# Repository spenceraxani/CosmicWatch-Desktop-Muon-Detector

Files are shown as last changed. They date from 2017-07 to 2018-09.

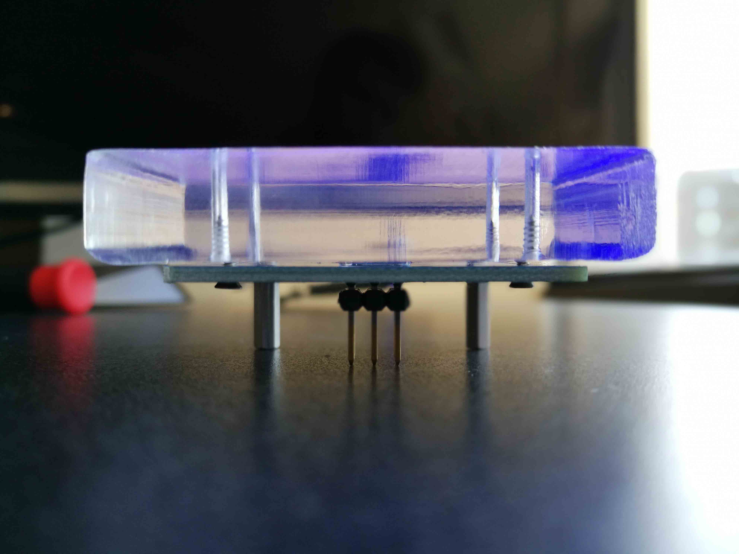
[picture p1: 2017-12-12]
Pictures/IMG_20171208_104722.jpg

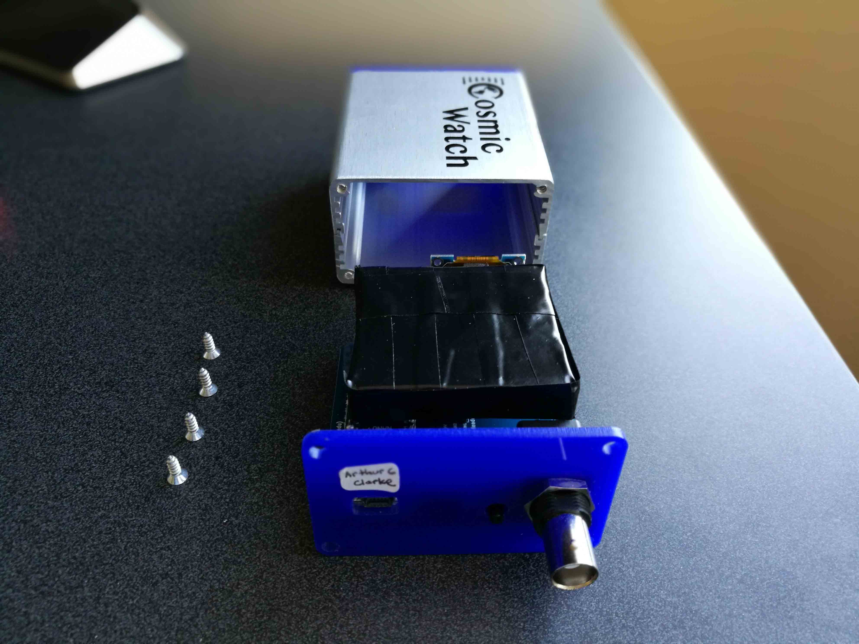
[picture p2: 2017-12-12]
Pictures/IMG_20171208_104146.jpg

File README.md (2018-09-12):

# (Outdated version) CosmicWatch-Desktop-Muon-Detector

The is an outdate version of the detector.
The latest version (v2) can be found here:
https://github.com/spenceraxani/CosmicWatch-Desktop-Muon-Detector-v2

This repository if for the supplementary material used to build the CosmicWatch Desktop Muon Detectors

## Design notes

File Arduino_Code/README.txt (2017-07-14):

This folder contains:
1. The Arduino Nano code. 
2. The CH340g driver from https://github.com/adrianmihalko/ch340g-ch34g-ch34x-mac-os-x-driver

In order to use the code, you must install the following libraries:
  1. Adafruit SSD1306     -- by Adafruit Version 1.0.1
  2. Adafruit GFX Library -- by Adafruit Version 1.0.2
  3. TimerOne             -- by Jesse Tane et al. Version 1.1.0

This can be done from the Arduino IDE: go to Tools, select
  1. Board = Arduino nano
  2. Port = the USB port that the Arduino is plugged into. If you don’t see it, you may need to install the CH340g driver

If you are using MAC OS, you need to also install the CH340g Driver. 

IF you are using Linux, you need to give permission to use your USB ports:
	In terminal: sudo chmod 666 /dev/ttyUSB0

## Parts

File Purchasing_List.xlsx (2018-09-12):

The following is the list of components used in the project. The links provided aren't necessarily the cheapest place to purchase the components, we've included it simply to indicate places where we have purchased them in the past.
Component List |  | Buy Extras
Item | Name | Required number | Discription | Link
1 | 49.9 Ohm resistor | 3 | RES SMD 49.9 OHM 1% 1/8W 0805 | Digikey Part Number: 311-49.9CRCT-ND
2 | 499 Ohm resistor | 1 | RES SMD 499 OHM 1% 1/8W 0805 | Digikey Part Number: 311-499CRCT-ND
3 | 1K resistor | 3 | RES SMD 1K OHM 1% 1/8W 0805 | Digikey Part Number: 311-1.00KCRCT-ND
4 | 10k resistor | 2 | RES SMD 10K OHM 1% 1/8W 0805 | Digikey Part Number: 311-10.0KCRCT-ND
5 | 100k resistor | 2 | RES SMD 100K OHM 1% 1/8W 0805 | Digikey Part Number: 311-100KCRCT-ND
6 | 226k resistor | 1 | RES SMD 226K OHM 1% 1/8W 0805 | Digikey Part Number: 311-226KCRCT-ND
7 | 5pF capacitor | 1 | CAP CER 5PF 50V NP0 0805 | Digikey Part Number: 1276-2552-1-ND
8 | 22pF capacitor | 1 | CAP CER 22PF 50V NP0 0805 | Digikey Part Number: 399-1113-1-ND
9 | 10nF capacitor | 5 | CAP CER 10000PF 50V X7R 0805 | Digikey Part Number: 311-1136-1-ND
10 | 0.1uF capacitor | 1 | CAP CER 0.1UF 50V X7R 0805 | Digikey Part Number: 399-1170-1-ND
11 | 0.47uF capacitor | 1 | CAP CER 0.47UF 50V X7R 0805 | Digikey Part Number: 399-8100-1-ND
12 | 1uF capacitor | 1 | CAP CER 1UF 50V Y5V 0805 | Digikey Part Number: 587-1308-1-ND
13 | 10uF capacitor | 1 | CAP CER 10UF 6.3V X5R 0805 | Digikey Part Number: 490-1718-1-ND
14 | 47uH inductor | 1 | FIXED IND 47UH 170MA 1.3 OHM SMD | Digikey Part Number: 490-4063-1-ND
15 | Schottky diode | 2 | DIODE SCHOTTKY 40V 500MA SOD123 | Digikey Part Number: MBR0540CT-ND
16 | 4 pin header | 1 | CONN FEMALE 4POS .100" R/A TIN | Digikey part number: S5440-ND
17 | 6-pin connector | 1 | 6-pin connector for SiPM PCB | Digikey Part Number: WM17457-ND
18 | 6-pin header | 1 | 6-pin header for Main PCB | Digikey Part Number: 1212-1229-ND
19 | Reset button | 1 | SWITCH TACTILE SPST-NO 0.02A 15V | Digikey part number: P12215S-ND
20 | BNC header | 1 | CONN BNC JACK R/A 50 OHM PCB | Digikey part number: WM5514-ND
21 | Standoff for SiPM PCB | 2 | 1/8" Hex Size, 3/8" Length, 0-80 Thread Size | McMasterCarr part number: 91780A027
22 | Standoff screws Main side | 4 | 0-80 Thread Size, 5/16" Long | McMasterCarr part number: 91771A056
23 | Plastic scintillator screws | 4 | 18-8 Stainless Steel, Number 0 Size, 5/16" Long | McMasterCarr part number: 92470A024
24 | DC-DC Booster | 1 | LT3461AES6#PBF | http://www.linear.com/product/LT3461A
25 | Op-Amp | 1 | LT1807IS8#PBF | http://www.linear.com/samples/LT1807
26 | 5mm LED | 1 | Any color, 5mm | https://www.amazon.com/gp/product/B01FDOBRU4/ref=ox_sc_act_title_2?ie=UTF8&psc=1&smid=A353AQG9I0DZD6
27 | Barrell Jack | 1 | 5.5mmx2.1mm 3Pins | https://www.amazon.com/gp/product/B00MJVIFS2/ref=ox_sc_act_title_4?ie=UTF8&psc=1&smid=AYQ5IQCXKV6BV
28 | 5mm LED holder | 1 | LED Light Mounting Holders | https://www.amazon.com/uxcell-Pieces-Plastic-Mounting-Holders/dp/B00K85965W
29 | Arduino Nano | 1 | ATmega328 CH340G | Check Ebay or Amazon
30 | OLED screen | 1 | 0.96" Inch I2c IIC OLED , 128x64 | https://www.amazon.com/Diymall-Serial-Display-Module-Arduino/dp/B01HHOAQ5A?s=electronics NOTE: VCC NEEDS TO BE THE 4th PIN ON THE OLED, IT CANNOT BE THE GND PIN. SOME MANUFACTURERS SWAP THE PINS.
31 | Tin Foil | 1 | 10x10cm of Aluminium foil for wrapping the Plastic scintilaltor | https://www.amazon.com/Reynolds-Wrap-Aluminum-Foil-Square/dp/B00UNT0Y2M
32 | Black electrical tap | ~1m | Black electrical tape for making the Plastic scintillator light-tight | https://www.amazon.com/Electrical-Tape-several-colors-Black/dp/B003ZWN5ZM
33 | Rubber feet | 4 | Silicon bumper for feet | https://www.amazon.com/VOVOV-Self-adhesive-Rubber-Bumpons-diameter/dp/B016GWHSBE
34 | SiPM | 1 | 6x6mm SiPM MicroFC-60035-SMT | http://sensl.com/estore/microfc-60035-smt/
35 | Plastic scintillator | 1 | 5x5x1 cm Plastic scintillator | You want something that peaks in the 400nm range.
36 | Optical Gel | <1ml | Small amount of optical gel. Vaciline might work. | Check ebay or amazon
37 | Aluminium Case (without faceplates) | 1 | Aluminium case, 2506H-2.9” | http://www.enclosuresandcasesinc.com/
38 | Main PCB + SiPM PCB | 1 | 2 layer, 10cm x 10cm, 1.6mm thickness, zipped files in PCB folder | https://www.elecrow.com/5pcs-2-layer-pcb.html
39 | Front and back faceplate | 1 | Endplates | You can 3d print them, or send the .dxf files to Elecrow and have them laser cut them. Or make them in a machine shop. Or http://www.enclosuresandcasesinc.com/ will make them

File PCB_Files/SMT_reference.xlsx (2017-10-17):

Main PCB
Component | value | Discription | Link | Comment
R1 | 10k | RES SMD 10K OHM 1% 1/8W 0805 | Digikey Part Number: 311-10.0KCRCT-ND | DC-DC Booster
R2 | 226k | RES SMD 226K OHM 1% 1/8W 0805 | Digikey Part Number: 311-226KCRCT-ND | DC-DC Booster
R3 | 499 | RES SMD 100 OHM 1% 1/8W 0805 | Digikey Part Number: 311-100CRCT-ND | Amplifying circuit
R4 | 1k | RES SMD 1K OHM 1% 1/8W 0805 | Digikey Part Number: 311-1.00KCRCT-ND
R5 | 10k | RES SMD 1K OHM 1% 1/8W 0805 | Digikey Part Number: 311-10.0KCRCT-ND | Amplifying circuit
R6 | 100k | RES SMD 100K OHM 1% 1/8W 0805 | Digikey Part Number: 311-100KCRCT-ND | Peak Detector Circuit
R7 | 100k | RES SMD 100K OHM 1% 1/8W 0805 | Digikey Part Number: 311-100KCRCT-ND | Peak Detector Circuit
R8 | 1k | RES SMD 1K OHM 1% 1/8W 0805 | Digikey Part Number: 311-1.00KCRCT-ND
R9 | 1k | RES SMD 1K OHM 1% 1/8W 0805 | Digikey Part Number: 311-1.00KCRCT-ND
D1 | 500ma diode | DIODE SCHOTTKY 40V 500MA SOD123 | Digikey Part Number: MBR0540CT-ND | Has direction
D2 | 500ma diode | DIODE SCHOTTKY 40V 500MA SOD123 | Digikey Part Number: MBR0540CT-ND | has direction
L1 | 47uH | FIXED IND 47UH 170MA 1.3 OHM SMD | Digikey Part Number: 490-4063-1-ND
C1 | 22pF | CAP CER 22PF 50V NP0 0805 | Digikey Part Number: 399-1113-1-ND | DC-DC Booster
C2 | 0.47uF | CAP CER 0.47UF 50V X7R 0805 | Digikey Part Number: 399-8100-1-ND | DC-DC Booster
C3 | 1uF | CAP CER 1UF 50V Y5V 0805 | Digikey Part Number: 587-1308-1-ND | DC-DC Booster
C4 | 10uF | CAP CER 10UF 6.3V X5R 0805 | Digikey Part Number: 490-1718-1-ND
C5 | 0.1uF | CAP CER 0.1UF 50V X7R 0805 | Digikey Part Number: 399-1170-1-ND
C6 | 10nF | CAP CER 1000PF 50V X7R 0805 | Digikey Part Number: 399-1147-1-ND | Peak Detector Circuit
C7 | 5pF | CAP CER 5pF 50V 0805 | Digikey Part Number: 1276-2552-1-ND
U1 | LT3461A | 3MHz booster | http://www.linear.com/product/LT3461A
U2 | LT1807IS8#PBF | 325MHz OpAmp | http://www.linear.com/product/LT1807
Reset | Reset button | SWITCH TACTILE SPST-NO 0.02A 15V | Digikey part number: P12215S-ND
Arduino_Nano | Arduino Nano | 16 MHz | Check Ebay or Amazon
BNC | BNC header | CONN BNC JACK R/A 50 OHM PCB | Digikey part number: WM5514-ND
OLED | 4 pin header | CONN FEMALE 4POS .100" R/A TIN | Digikey part number: S5440-ND
LED | LED light | Any color, 5mm | https://www.amazon.com/gp/product/B01FDOBRU4/ref=ox_sc_act_title_2?ie=UTF8&psc=1&smid=A353AQG9I0DZD6
Header | 6pin connector | SOCKET 7 MM SOLDER TAIL DOUBLE | Digikey Part Number: 1212-1229-ND
SiPM PCB
Component | value | Discription | Link | Comment
R1 | 49.9 | RES SMD 49.9 OHM 1% 1/8W 0805 | Digikey Part Number: 311-49.9CRCT-ND
R2 | 49.9 | RES SMD 49.9 OHM 1% 1/8W 0805 | Digikey Part Number: 311-49.9CRCT-ND
R2 | 49.9 | RES SMD 49.9 OHM 1% 1/8W 0805 | Digikey Part Number: 311-49.9CRCT-ND
C1 | 10 nF | CAP CER 10000PF 50V X7R 0805 | Digikey Part Number: 311-1136-1-ND
C2 | 10 nF | CAP CER 10000PF 50V X7R 0805 | Digikey Part Number: 311-1136-1-ND
C3 | 10 nF | CAP CER 10000PF 50V X7R 0805 | Digikey Part Number: 311-1136-1-ND
C4 | 10 nF | CAP CER 10000PF 50V X7R 0805 | Digikey Part Number: 311-1136-1-ND
U1 |  | SiPM MicroFC-60035-SMT | SENSL
Header | 6-pin connector | WM17457-ND | WM17457-ND

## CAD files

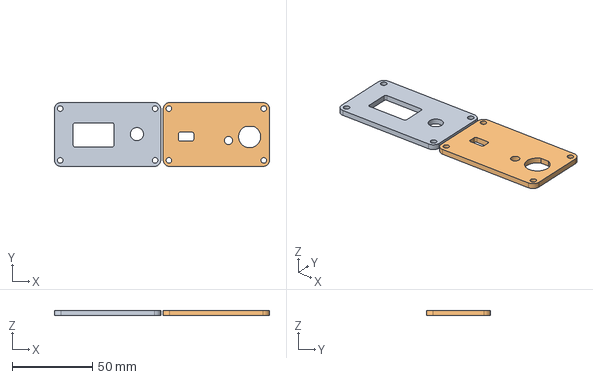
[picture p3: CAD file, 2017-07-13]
Enclosure_Files/Endplates.step
134.3 x 39.9 x 3.00 mm
Endplates
Endplates001

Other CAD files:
Enclosure_Files/Endplates.dxf
Enclosure_Files/Endplates.ipt
Enclosure_Files/Endplates.stl
Enclosure_Files/Endplates.stp

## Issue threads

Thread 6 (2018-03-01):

### ISSUE TITLE
Single LED and count on main board test

### ISSUE THREAD

**Issue by johnddias** [spenceraxani/CosmicWatch-Desktop-Muon-Detector#6]
Looking for any tips, please.  The main PCB is assembled and when I plug it in I see the LED blink once and the screen reports one measurement.  from the instructions I was expecting a solid LED and a negative count with the SPiM disconnected, what could be wrong?  Thanks

**Comment by spenceraxani** [comment]
Hi,

Not to worry, it’s probably fine. As long as you see that the CosmicWatch splash screen appears on the OLED and that you are seeing roughly +29.5V on the HV to GND pins on the 6-pin header , that’s about as much as you can test until you plug the SiPM in. 

An older version of the code wasn’t taking the dead time into account properly, and that is what was causing the negative count rate. This has been fixed with the updated Arduino code. 

Thanks,

Spencer

**Comment by johnddias** [comment]
Thanks Spencer.  I did get my SiPM ready and plugged in but getting the same result on the display.  I'm waiting for a scope to test things out before I give up hope.

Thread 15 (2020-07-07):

### ISSUE TITLE
PCB populating reference clarification

### ISSUE THREAD

**Issue by jparshook** [spenceraxani/CosmicWatch-Desktop-Muon-Detector#15]
On the PCB populating reference sheet, C14 is listed as a resistor (0 Ohm jumper) but is shown as a capacitor on the schematic. Could you please clarify the correct part for C14?

**Comment by spenceraxani** [comment]
Hi,

C14 can just be shorted with a 0Ohm resistor or a wire. 

Thanks,

Spencer

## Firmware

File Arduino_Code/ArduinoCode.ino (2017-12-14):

/*
Desktop Muon Counter Arduino Code
Questions?
Spencer N. Axani 
saxani@mit.edu

Requirements: Sketch->Include->Manage Libraries:
  1. Adafruit SSD1306     -- by Adafruit Version 1.0.1
  2. Adafruit GFX Library -- by Adafruit Version 1.0.2
  3. TimerOne             -- by Jesse Tane et al. Version 1.1.0
*/

#include <Adafruit_SSD1306.h>
#include <Adafruit_GFX.h>
#include <Wire.h>
#include <SPI.h>
#include <TimerOne.h>  
#include <EEPROM.h>

const byte OLED = 1;                    // Turn on/off the OLED [1,0] (Set to 0 to improve time)
const byte LED  = 0;                    // Turn on/off the LED delay [1,0] (Set to 0 to improve time)
const int SIGNAL_THRESHOLD = 20;        // Min threshold to trigger on
const int LED_BRIGHTNESS = 255;          // Change the brightness on the LED [0-255]. 5 is a dim value.


//This calibration is for 499, 5pF, 10k
//const float cal[] = {4.0614902396231111e-14, -7.8414735932155768e-11, 5.6819206951234577e-08, -1.7873823684604088e-05, 0.0029455520399522652, 0.01701073093454207, 26.268331951783924};
//This calibration is for 499, 5pF, 10k
const float cal[] = {9.038130548712698e-15, -1.4599909946491252e-12, -1.2626490003703338e-08, 1.1406923013075114e-05, -0.002891003749200569, 0.5003740521722947, 15.615470780166067};


//INTERUPT SETUP
#define TIMER_INTERVAL 1000000          // Every 1,000,000 us the timer will update the clock on the screen

//OLED SETUP
#define OLED_RESET 10             
Adafruit_SSD1306 display(OLED_RESET);   // Setup the OLED


//initialize variables
char detector_name[40];

unsigned long time_stamp                      = 0L;
unsigned long measurement_deadtime            = 0L;
unsigned long time_measurement                = 0L;      // Time stamp
unsigned long interrupt_timer                 = 0L;      // Time stamp
unsigned long start_time                      = 0L;      // Reference time for all the time measurements
unsigned long total_deadtime                  = 0L;      // total measured deadtime
unsigned long waiting_t1                      = 0L;
unsigned long measurement_t1;
unsigned long measurement_t2;
float sipm_voltage =0;
unsigned long count                           = 0L;      // A tally of the number of muon counts observed
float last_sipm_voltage                          = 0;

byte waiting_for_interupt = 0;

void setup() {
  ADCSRA &= ~(bit (ADPS0) | bit (ADPS1) | bit (ADPS2));    // clear prescaler bits
  ADCSRA |= bit (ADPS1);                                   // Set prescaler to 4  
  Serial.begin(9600);
  
  display.begin(SSD1306_SWITCHCAPVCC, 0x3C);               // Begin the OLED screen
  
  if (OLED == 1)
  {
      display.setRotation(2);                       // 2 = upside down; 0 = rightside down
      OpeningScreen();
      delay(2000); 
      display.setTextSize(1);
  }
  
  pinMode(3, OUTPUT);
  
  get_detector_name(detector_name);
  Serial.println(detector_name);
  
  analogRead(A0);
  
  start_time = millis();
  Timer1.initialize(TIMER_INTERVAL);             // Initialise timer 1
  Timer1.attachInterrupt(timerIsr);              // attach the ISR routine
}

// The loop runs continuously, looking for a signal to pass SIGNAL_THRESHOLD
void loop() 
{
  while (1) 
  {
    if (analogRead(A0) > SIGNAL_THRESHOLD)
    { 
      count++;      
      time_stamp = millis() - start_time; 
      float avg_adc_measurement = (analogRead(A0) + analogRead(A0) + analogRead(A0) + analogRead(A0)) / 4.;
      measurement_deadtime = total_deadtime;
      
      if((interrupt_timer + 1000 - millis()) < 15)
      { 
          waiting_t1 = millis();
          waiting_for_interupt = 1;
          delay(30);
          waiting_for_interupt = 0;
      }
      measurement_t1 = micros();
      analogWrite(3, LED_BRIGHTNESS);
      sipm_voltage = get_sipm_voltage(avg_adc_measurement);
      last_sipm_voltage = sipm_voltage; 
      Serial.println((String)count + " " + time_stamp+ " " + avg_adc_measurement+ " " + sipm_voltage + " " + total_deadtime);

      
      digitalWrite(6, LOW);  
      digitalWrite(3, LOW);
      while((analogRead(A0)+analogRead(A0)+analogRead(A0))/3. > (9)){continue;}
      
      total_deadtime += (micros() - measurement_t1 + 1062) / 1000.;
                       
    }
  }
}
  

//TIMER INTERUPT
void timerIsr() 
{
  interrupts();
  interrupt_timer                       = millis();
  if (waiting_for_interupt == 1){total_deadtime += (millis() - waiting_t1);}
  waiting_for_interupt = 0;
  if (OLED == 1){get_time();}
}

// This function updates the OLED screen with the stats.
void get_time() {
  unsigned long int OLED_t1        = micros();
  float count_average         = 0;
  float count_std             = 0;

  if (count > 0.) 
  {
  count_average = count / ((interrupt_timer - start_time - total_deadtime) / 1000.);
  count_std     = sqrt(count) / ((interrupt_timer - start_time - total_deadtime) / 1000.);
  }
   else 
  {
      count_average   = 0;
      count_std       = 0;
  }
  
  display.setCursor(0, 0);
  display.clearDisplay();
  display.print(F("Total Count: "));
  display.println(count);
  display.print(F("Uptime: "));

  int minutes                 = ((interrupt_timer- start_time) / 1000 / 60) % 60;
  int seconds                 = ((interrupt_timer- start_time) / 1000) % 60;
  char min_char[4];
  char sec_char[4];
  
  sprintf(min_char, "%02d", minutes);
  sprintf(sec_char, "%02d", seconds);

  display.println((String) (interrupt_timer / 1000 / 3600) + ":" + min_char + ":" + sec_char);

  if (count == 0) 
  {
      display.println(F("Initializing..."));
  }
  
  else 
  {
      if (last_sipm_voltage > 180) 
      {
          display.print(F("===---- WOW! ----==="));
      }

      else 
      {
       for (int i = 1; i <=  (last_sipm_voltage + 10) / 10; i++) {display.print(F("-"));}
      }
      display.println(F(""));
  }

  char tmp_average[4];
  char tmp_std[4];

  int decimals = 2;
  if (count_average < 10) {decimals = 3;}
  
  dtostrf(count_average, 1, decimals, tmp_average);
  dtostrf(count_std, 1, decimals, tmp_std);
   
  display.print(F("Rate: "));
  display.print((String)tmp_average);
  display.print(F("+/-"));
  display.println((String)tmp_std);
  display.display();
  
  total_deadtime                      += (micros() - OLED_t1 +73.)/1000.;
}


// This function runs the splash screen as you turn on the detector
void OpeningScreen(void) {
  display.setTextSize(2);
  display.setTextColor(WHITE);
  display.setCursor(8, 0);
  display.clearDisplay();
  display.print(F("Cosmic \n     Watch"));
  display.display();
  display.setTextSize(1);
  display.clearDisplay();
}

// This function converts the measured ADC value to a SiPM voltage
//float get_sipm_voltage(float x) 
//{
//    return cal[0] * pow(x, 6) + cal[1] * pow(x, 5) + cal[2] * pow(x, 4) + cal[3] * pow(x, 3) + cal[4] * pow(x, 2) + cal[5] * pow(x, 1) + cal[6];
//}

float get_sipm_voltage(float adc_value)
{
  float voltage = 0;
  for (int i = 0; i < (sizeof(cal)/sizeof(float)); i++) {
    voltage += cal[i] * pow(adc_value,(sizeof(cal)/sizeof(float)-i-1));
    }
    return voltage;
}


// This function reads the first 40 characters written to the EEPROM, where the name is stored
// To change the name of the detector, upload the Naming.ino Arduino code.
boolean get_detector_name(char* det_name) 
{
    byte ch;                              // byte read from eeprom
    int bytesRead = 0;                    // number of bytes read so far
    ch = EEPROM.read(bytesRead);          // read next byte from eeprom
    det_name[bytesRead] = ch;               // store it into the user buffer
    bytesRead++;                          // increment byte counter

    while ( (ch != 0x00) && (bytesRead < 40) && ((bytesRead) <= 511) ) 
    {
        ch = EEPROM.read(bytesRead);
        det_name[bytesRead] = ch;           // store it into the user buffer
        bytesRead++;                      // increment byte counter
    }
    if ((ch != 0x00) && (bytesRead >= 1)) {det_name[bytesRead - 1] = 0;}
    return true;
}

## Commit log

2017-07-13 adding the new files
    [Endplates.dxf, Endplates.ipt, Endplates.step, Endplates.stl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]
2017-07-20 updating purchasing list
    [Purchasing_List.xlsx]
2017-12-14 Updated Arduino code -- new calibration and OLED
2018-01-18 should be 47uH inductor
    [Purchasing_List.xlsx]
2018-02-07 updated DC Booster part number
    [Purchasing_List.xlsx]
2018-03-09 Create variable RESET_THRESHOLD
    The appropriate thresholds to set varies depending on
    the power source. To make it easy to adjust we create
    a variable for the reset threshold (the threshold for
    which to begin allowing for the next trigger).
2018-04-01 removed discrepency in Arduino Code
